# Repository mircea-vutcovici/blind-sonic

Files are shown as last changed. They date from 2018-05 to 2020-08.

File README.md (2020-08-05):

[English](https://github.com/mircea-vutcovici/blind-sonic) [română](https://github.com/mircea-vutcovici/blind-sonic/blob/master/README.ro.md)
# BlindSonic
Device used for blind people to find objects using an ultrasonic distance sensor

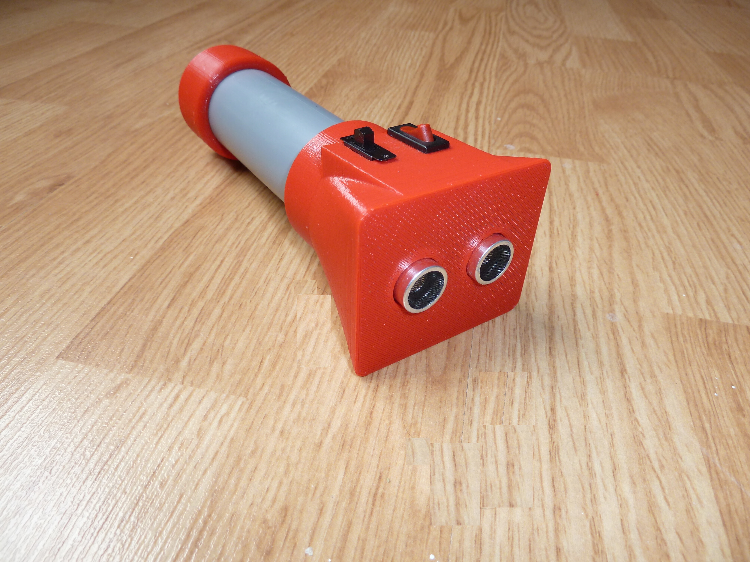
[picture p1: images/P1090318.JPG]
BlindSonic picture


[TV NEWS BUZAU - Ultrasonic device for visually impaired - 06 12 2017 (Romanian)](https://youtu.be/FoDEJMZK1bs)

## History
This project is created by Cosmin Vatra. He did all the work of testing and creating the first prototypes.
Here, with his permission, I am just publising it.

## Bill of materials
The list of materials required: [English](https://github.com/mircea-vutcovici/blind-sonic/blob/master/BOM.md), [română](https://github.com/mircea-vutcovici/blind-sonic/blob/master/BOM.ro.md)

## Links to similar projects
* [How to Make a Smart Cane for the Visually Impaired With Arduino](https://maker.pro/projects/arduino/arduino-smart-cane-for-the-blind)
* [WeWALK Smart Cane](https://www.indiegogo.com/projects/revolutionary-smart-cane-for-the-visually-impaired#/)

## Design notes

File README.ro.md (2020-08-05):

[English](https://github.com/mircea-vutcovici/blind-sonic) [română](https://github.com/mircea-vutcovici/blind-sonic/blob/master/README.ro.md)
# BlindSonic
Dispositiv pentru orientare destinat persoanelor care nu vad.

fotografie a BlindSonic

[TV NEWS BUZAU - INTERVIURI ALTFEL - Aparat cu ultrasunete pentru nevazatori - 06 12 2017](https://youtu.be/FoDEJMZK1bs)

## Cronologie
Acest proiect a fost facut de Cosmin Vatra. El a conceput si facut primele prototipuri.
Cu permisiunea lui am publicat aceste detalii.

## Lista de materiale
[English](https://github.com/mircea-vutcovici/blind-sonic/blob/master/BOM.md), [română](https://github.com/mircea-vutcovici/blind-sonic/blob/master/BOM.ro.md)

## Legaturi catre proiecte similare
* [How to Make a Smart Cane for the Visually Impaired With Arduino](https://maker.pro/projects/arduino/arduino-smart-cane-for-the-blind)
* [WeWALK Smart Cane](https://www.indiegogo.com/projects/revolutionary-smart-cane-for-the-visually-impaired#/)

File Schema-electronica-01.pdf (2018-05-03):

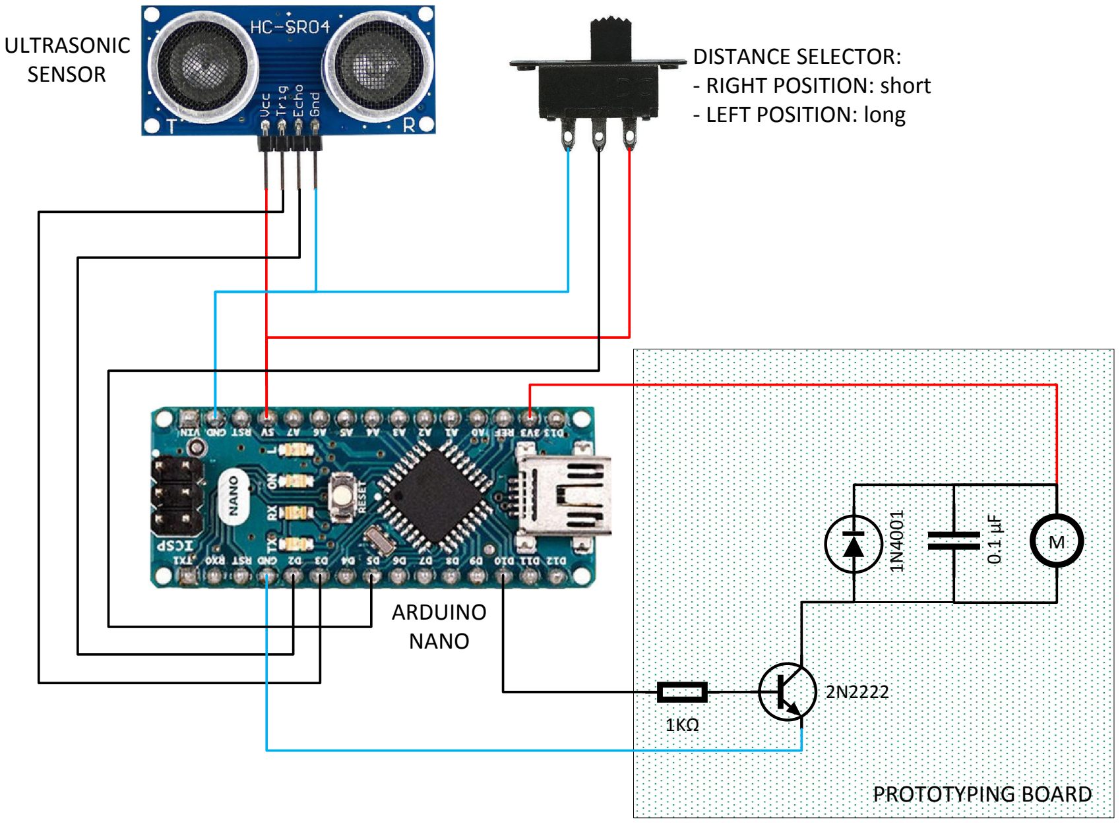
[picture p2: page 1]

PROTOTYPING BOARD ⁰.1 µF

1KΩ

2N2222

1N4001
M

ARDUINO
NANO

ULTRASONIC
SENSOR

DISTANCE SELECTOR:
- RIGHT POSITION: short
- LEFT POSITION: long

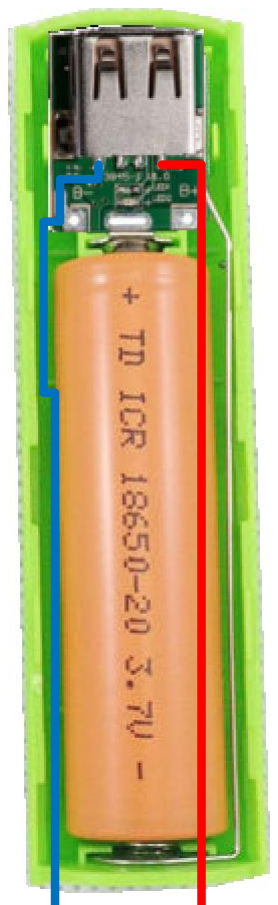
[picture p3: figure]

On/off switch

POWER BANK

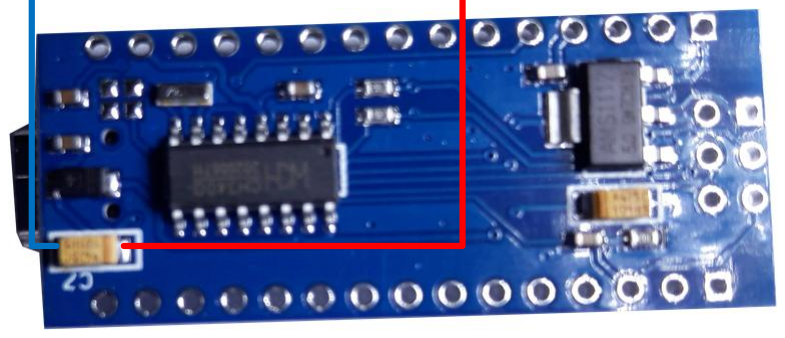
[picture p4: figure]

ARDUINO
NANO

## VIBRATION MOTOR PROTOTYPING BOARD

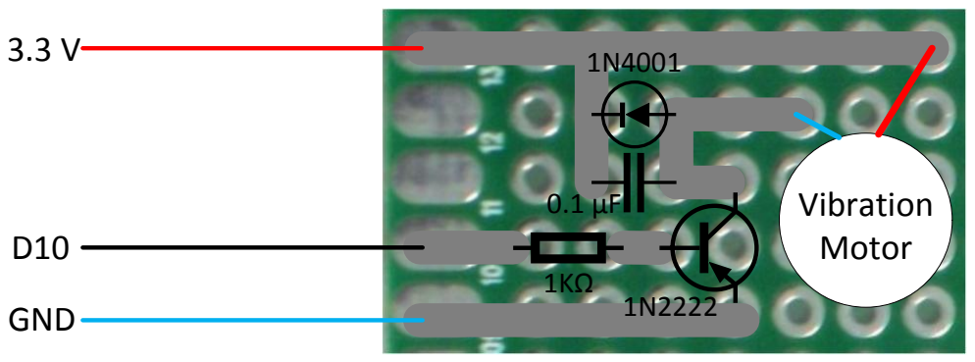
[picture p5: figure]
GND; Vibration Motor

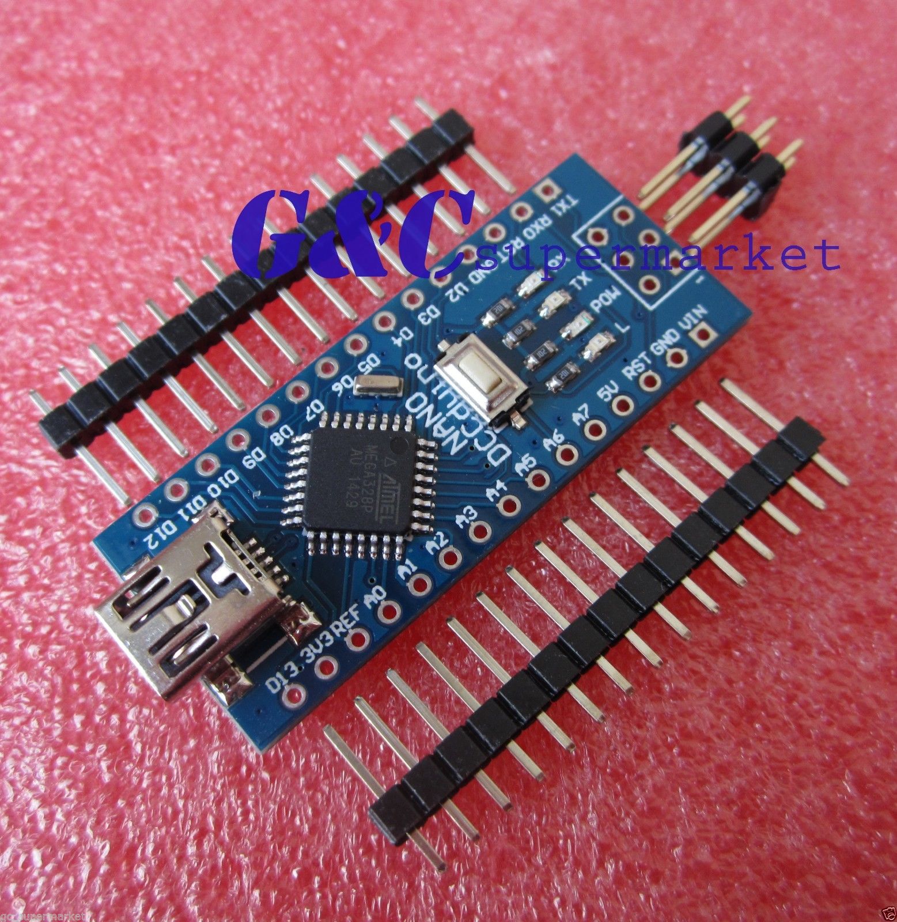
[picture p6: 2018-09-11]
images/ATmega328P.jpg

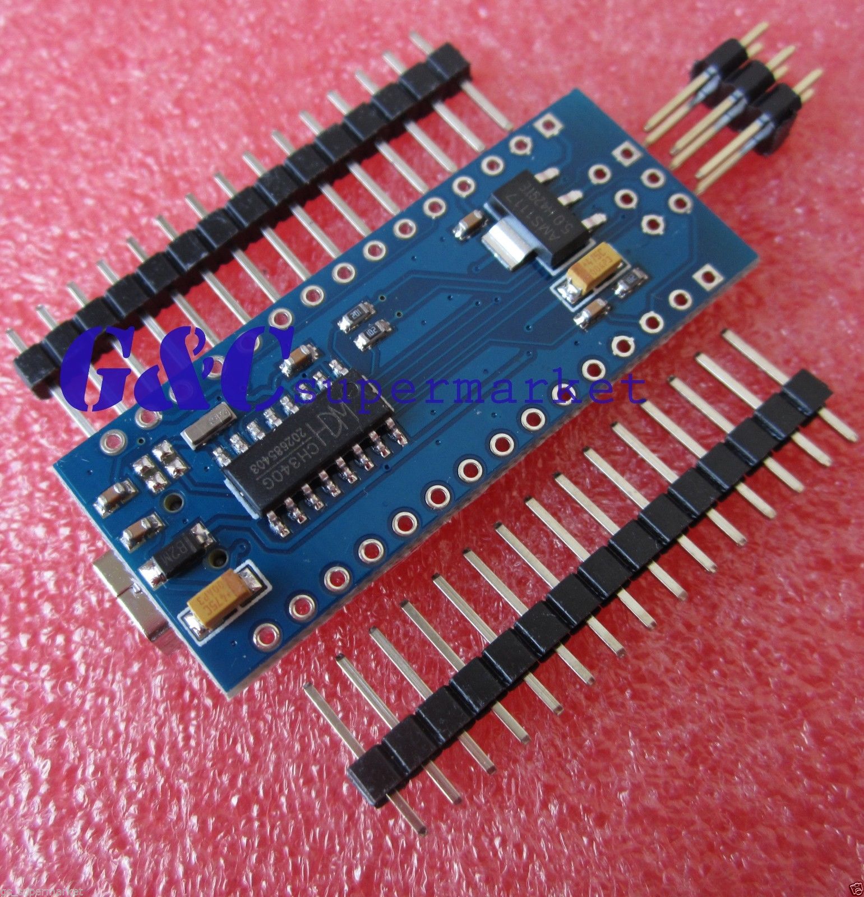
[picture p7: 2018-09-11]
images/CH340G.jpg

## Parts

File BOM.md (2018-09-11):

# Bill of materials

1. [Arduino Nano ATmega328P microcontroller with CH340G USB-serial interface](https://www.ebay.com/itm/MINI-USB-Nano-V3-0-ATmega328P-CH340G-5V-16M-Micro-controller-board-Arduino-M47/291548871778?ssPageName=STRK%3AMEBIDX%3AIT&_trksid=p2057872.m2749.l2649) - MINI USB Nano V3.0 [ATmega328P](images/ATmega328P.jpg) [CH340G](images/CH340G.jpg) 5V 16M Micro-controller board Arduino M47

2. [Ultrasonic Sensor HC-SR04](https://www.ebay.com/itm/1-2-5-10PCS-Ultrasonic-Module-HC-SR04-Distance-Transducer-Sensor-for-Arduino/112546863866?ssPageName=STRK%3AMEBIDX%3AIT&var=412941347380&_trksid=p2057872.m2749.l2649)

3. Vibrating Micro Motor (any small motor which works at 3V DC; E. g.:
   1. (https://www.ebay.com/itm/10x-Coin-Flat-Vibrating-Micro-Motor-DC-3V-Fit-For-Pager-and-Cell-Phone-Mobile/142116085316?ssPageName=STRK%3AMEBIDX%3AIT&_trksid=p2057872.m2749.l2649)

   2. (https://www.ebay.com/itm/2PCS-4x8mm-DC-1-3V-Micro-Coreless-Vibrating-Vibrator-Vibration-Motor-5400RPM-Hot/382216717924?epid=2219921886&hash=item58fde44664:g:adQAAOSwn1FZqNMO)

   3. (https://www.ebay.com/itm/LOT-OF-10-NEW-Vibrator-vibration-Silent-Motor-Replacement-for-iPhone-5-VERIZON/380685797564?epid=1731755586&hash=item58a2a448bc:g:ojsAAOxymHRRwjqP)

4. [Power bank box case with charger circuit](https://www.ebay.com/itm/2600mAh-Box-Case-Kit-Bank-Power-18650-Battery-HOT-DIY-Charger-USB-For-All-Phone/332198327461?ssPageName=STRK%3AMEBIDX%3AIT&var=541225900261&_trksid=p2057872.m2749.l2649)

5. [Rechargable battery to install in the power case](https://www.ebay.com/itm/10x-PKCELL-18650-Li-ion-Rechargeable-Battery-Bater%C3%ADa-Pila-3-7V-2200mAh-Flat-Top/131942744626?ssPageName=STRK%3AMEBIDX%3AIT&_trksid=p2057872.m2749.l2649)

6. [On/off switch](https://www.ebay.com/itm/10x-Red-Button-ON-OFF-SPST-2-Pin-Snap-In-Boat-Rocker-Switch-12A-125V-6A-250V-AC/310568187206?hash=item484f4e7546:g:nx8AAOSwvTBZuWxZ)

7. [3 state DPDT switch](https://www.ebay.com/itm/10-Pcs-6-Pins-2-Positions-DPDT-On-On-Mini-Slide-Switch-S6T6-K7L9/322869731297?epid=1569373440&hash=item4b2c891fe1:g:ThAAAOSwlaRaAjbD)

Following components can be purchased from a local electronics store as they are cheap. Make sure you buy the [through hole](https://en.wikipedia.org/wiki/Through-hole_technology) version and not the [SMD](https://en.wikipedia.org/wiki/Surface-mount_technology) version.

6. [2N2222](https://en.wikipedia.org/wiki/2N2222) Transistor 

7. Rectifier Diode 1N40001

8. Capacitor 0.1 μF (micro)

9. Resistor 1kΩ

10. Wire - best is speaker wire, like (https://www.ebay.com/itm/10M-RED-BLACK-SPEAKER-CABLE-WIRE-SOUND-CAR-HOME-STEREO-HIFI-CAR-AUDIO-SYSTEM/222514147451?epid=1495419495&hash=item33cee0707b:g:aaIAAOSwEH9ZaD8~) It is better to buy from the local electronics shop (not online) as you can find better quality then ones found online.

11. Prototype [PCB](https://en.wikipedia.org/wiki/Printed_circuit_board) like (https://www.ebay.com/itm/5Pcs-Printed-Circuit-Board-Prototype-Test-PCB-Stripboard-Electronic-Panel-Craft/272582657185?epid=606877017&hash=item3f773144a1:g:U38AAOSwdGFYwLKk)

12. Hot melt glue, like (https://www.ebay.com/itm/10pcs-Hot-Melt-Glue-Stick-7mm-Adhesive-for-Craft-Electric-Tool-Heating-Glue-Gun/112539537917?hash=item1a33e111fd:g:3NoAAOSwuU9Zn4KR)

1

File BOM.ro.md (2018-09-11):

# Lista de materiale

1. [Controler Arduino Nano ATmega328P cu interfata USB-serială CH340G](https://www.ebay.com/itm/MINI-USB-Nano-V3-0-ATmega328P-CH340G-5V-16M-Micro-controller-board-Arduino-M47/291548871778?ssPageName=STRK%3AMEBIDX%3AIT&_trksid=p2057872.m2749.l2649) - MINI USB Nano V3.0 [ATmega328P](images/ATmega328P.jpg) [CH340G](images/CH340G.jpg) 5V 16M Micro-controller board Arduino M47

2. [Senzor ultrasonic HC-SR04](https://www.ebay.com/itm/1-2-5-10PCS-Ultrasonic-Module-HC-SR04-Distance-Transducer-Sensor-for-Arduino/112546863866?ssPageName=STRK%3AMEBIDX%3AIT&var=412941347380&_trksid=p2057872.m2749.l2649)

3. Motor vibrator (orice motor mic care merge alimentat la 3 VCC; Exemple:
   1. (https://www.ebay.com/itm/10x-Coin-Flat-Vibrating-Micro-Motor-DC-3V-Fit-For-Pager-and-Cell-Phone-Mobile/142116085316?ssPageName=STRK%3AMEBIDX%3AIT&_trksid=p2057872.m2749.l2649)

   2. (https://www.ebay.com/itm/2PCS-4x8mm-DC-1-3V-Micro-Coreless-Vibrating-Vibrator-Vibration-Motor-5400RPM-Hot/382216717924?epid=2219921886&hash=item58fde44664:g:adQAAOSwn1FZqNMO)

   3. (https://www.ebay.com/itm/LOT-OF-10-NEW-Vibrator-vibration-Silent-Motor-Replacement-for-iPhone-5-VERIZON/380685797564?epid=1731755586&hash=item58a2a448bc:g:ojsAAOxymHRRwjqP)

4. [Carcasă powerbank cu sistem de încârcare](https://www.ebay.com/itm/2600mAh-Box-Case-Kit-Bank-Power-18650-Battery-HOT-DIY-Charger-USB-For-All-Phone/332198327461?ssPageName=STRK%3AMEBIDX%3AIT&var=541225900261&_trksid=p2057872.m2749.l2649)

5. [Acumulator care se montează în carcasa powerbank](https://www.ebay.com/itm/10x-PKCELL-18650-Li-ion-Rechargeable-Battery-Bater%C3%ADa-Pila-3-7V-2200mAh-Flat-Top/131942744626?ssPageName=STRK%3AMEBIDX%3AIT&_trksid=p2057872.m2749.l2649)

6. [Comutator on/off](https://www.ebay.com/itm/10x-Red-Button-ON-OFF-SPST-2-Pin-Snap-In-Boat-Rocker-Switch-12A-125V-6A-250V-AC/310568187206?hash=item484f4e7546:g:nx8AAOSwvTBZuWxZ)

7. [Selector cu 3 poziții](https://www.ebay.com/itm/10-Pcs-6-Pins-2-Positions-DPDT-On-On-Mini-Slide-Switch-S6T6-K7L9/322869731297?epid=1569373440&hash=item4b2c891fe1:g:ThAAAOSwlaRaAjbD)

Următoarele componente le poți cumpăra de oriunde întrucât sunt foarte ieftine (< 1$/100 buc). Să ai grijă să nu cumperi SMD (din cele mici care se lipesc automat în fabrică), întrucât se lipesc dificil.

6. Tranzistor 2N2222 

7. Diodă 1N40001 

8. Condensator 0.1 uF (micro)

9. Rezistor 1k

10. Cablu - îți recomand cablu pentru boxe gen (https://www.ebay.com/itm/10M-RED-BLACK-SPEAKER-CABLE-WIRE-SOUND-CAR-HOME-STEREO-HIFI-CAR-AUDIO-SYSTEM/222514147451?epid=1495419495&hash=item33cee0707b:g:aaIAAOSwEH9ZaD8~) Eu prefer să cumpăr direct de la magazin (nu online) întrucât sunt unele proaste și se rup repede după câteva îndoituri/dezdoituri.

11. Cablaj de test de genul (https://www.ebay.com/itm/5Pcs-Printed-Circuit-Board-Prototype-Test-PCB-Stripboard-Electronic-Panel-Craft/272582657185?epid=606877017&hash=item3f773144a1:g:U38AAOSwdGFYwLKk)

12. Hot melt glue gen (https://www.ebay.com/itm/10pcs-Hot-Melt-Glue-Stick-7mm-Adhesive-for-Craft-Electric-Tool-Heating-Glue-Gun/112539537917?hash=item1a33e111fd:g:3NoAAOSwuU9Zn4KR)

13. Fludor

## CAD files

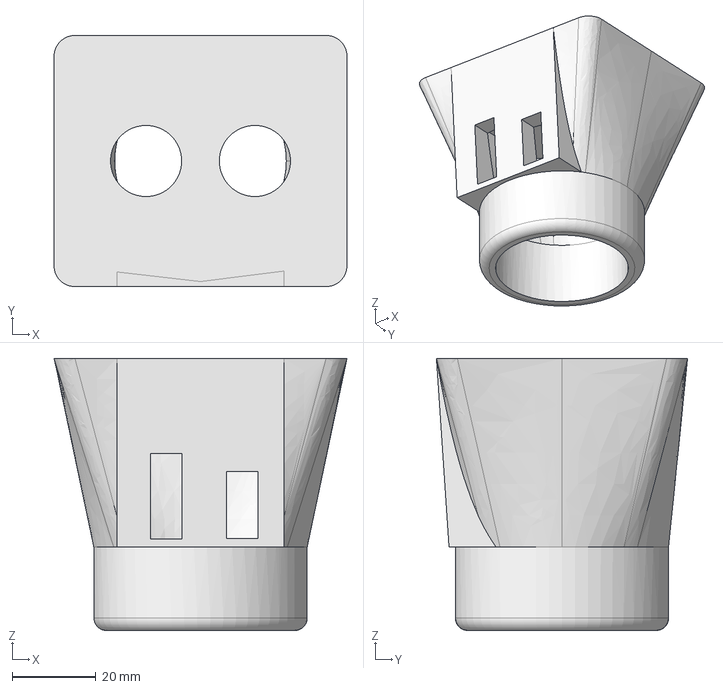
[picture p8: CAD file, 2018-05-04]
Capat senzor 05.FCStd
70.0 x 60.0 x 65.0 mm

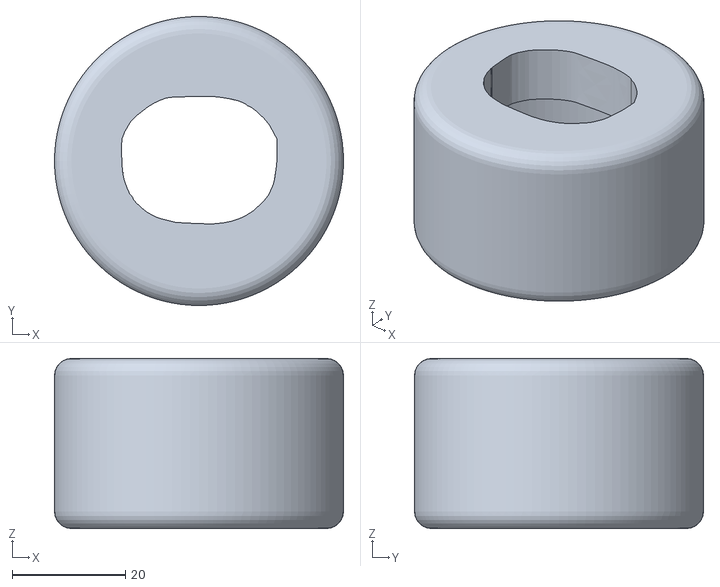
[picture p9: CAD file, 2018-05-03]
stl/Capat-power-bank (1).stl
51.0 x 51.0 x 30.0

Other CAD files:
Capat power bank 02.FCStd
stl/Capat-senzor-05 (1).stl
stl/Capat-senzor-05.stl

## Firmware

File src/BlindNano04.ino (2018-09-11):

const int trigPin = 3;
const int echoPin = 2;
const int MotVib=10; //Vibrating motor control pin
const int Mod1Pin=5; //Distance selector control pin
const int Dmax1=70; //The maximum distance on "short distance mode"
const int Dmin1=25; //The minimum distance on "short distance mode" 
const int Dmax2=200;//The maximum distance on "long distance mode"
const int Dmin2=25; //The minimum distance on "long distance mode"
const int Pauza=30; //Time between two Trig's
long duration, duration_last;
int distance;
int frecventa;



void setup() {

pinMode(trigPin, OUTPUT); // Trig pin set for output
pinMode(echoPin, INPUT); // Echo pin set for input
pinMode(MotVib, OUTPUT); // Vibration Motor pin set for output
pinMode(Mod1Pin, INPUT); // Distance Selector Mode pin for input

//Serial.begin(9600);  //To be used only for diagnostic purposes
}

void loop() {

if(digitalRead(Mod1Pin)==HIGH)
{
  //If the distance selector is set to short distance: 
duration_last=8000;
for(int i=0;i<6;i++)
{
digitalWrite(trigPin, LOW);
delayMicroseconds(2);
// Trig pin is set to HIGH for 10 micro seconds
digitalWrite(trigPin, HIGH);
delayMicroseconds(10);
digitalWrite(trigPin, LOW);
//Echo pin is read. It returns the time between the emision and the reception of the ultrasonic wave in microseconds
//If 7000 microseconds are passing and there is no pulsein, the function returns 0 (timeout).
duration = pulseIn(echoPin, HIGH, 7000);
if(duration!=0)
{
  if(duration<duration_last)
  {
    duration_last=duration;
  }
}

}

 //distance calculation using sound speed 0.034 cm/us:
distance= ( duration_last*0.034)/2;  
//Serial.println(distance); //To be used only for diagnostic

//Send pulses to the vibration motor, with a frequency inversely proportional to the distance  
if(distance<Dmax1)
{
 if(distance>Dmin1)
 {
 frecventa=100+155*(Dmax1-distance)/(Dmax1-Dmin1);
  analogWrite(MotVib, frecventa);

 }
 else
 {
  //If the distance selector is set to long distance:
  analogWrite(MotVib,255);
 }
}
else
{
  analogWrite(MotVib, 0);
}
}

else
{
  duration_last=16000;
for(int i=0;i<12;i++)
{
digitalWrite(trigPin, LOW);
delayMicroseconds(2);
// Trig pin is set to HIGH for 10 micro seconds
digitalWrite(trigPin, HIGH);
delayMicroseconds(10);
digitalWrite(trigPin, LOW);
//Echo pin is read. It returns the time between the emision and the reception of the ultrasonic wave in microseconds
//If 15000 microseconds are passing and there is no pulsein, the function returns 0 (timeout).
duration = pulseIn(echoPin, HIGH, 15000);
if(duration!=0)
{
  if(duration<duration_last)
  {
    duration_last=duration;
  }
}

}

 //distance calculation using sound speed 0.034 cm/us:
distance= ( duration_last*0.034)/2;
//Serial.println(distance); //To be used only for diagnostic purposes

if(distance<Dmax2)
{
 if(distance>Dmin2)
 {
 frecventa=100+155*(Dmax2-distance)/(Dmax2-Dmin2);
 analogWrite(MotVib, frecventa);
 }
 else
 {
 analogWrite(MotVib,255);
 }
}
else
{
  analogWrite(MotVib, 0);
}
}

}

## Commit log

2018-04-12 Attribution. List of materials
2018-05-03 Adding some binary files. We will add the source and remove the binary files later.
    [Capat-power-bank (1).stl, Capat-power-bank.stl, Capat-senzor-05 (1).stl, Capat-senzor-05.stl]
2018-05-04 Added FreeCAD sources
    [Capat power bank 02.FCStd, Capat senzor 05.FCStd]
2018-07-23 Image of the device
2018-09-11 Added images of ATmega328P and CH340G integrated circuits
2018-09-11 Added Arduino firmware
